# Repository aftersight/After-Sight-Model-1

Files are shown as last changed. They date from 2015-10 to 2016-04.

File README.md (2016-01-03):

# After-Sight-Model-1
Repository for Code/PCB design/3D printed models/Assembly Guide for the After Sight Model 1. go to after-sight.com for additional information

If you would like to contribute, please first go to the raspberry pi forum and post there to introduce yourself. 

https://www.raspberrypi.org/forums/viewtopic.php?f=41&t=49634

What I recommend is to download a current filesystem image. Go to after-sight.com/support

Download the zipped image, extract it, and then burn it to a micro SD card with a program like win32diskimager. 

Put the micro SD into the After Sight Model 1, and fire away. 

If you don't do that, there is a laundry list of dependencies to deal with. 

If you need an after sight model 1 (hardware), email mike.mcwilliams@after-sight.com.

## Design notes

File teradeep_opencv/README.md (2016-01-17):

# demonstration application - Embedded

This is our May 2015 top neural network for large-scale object recognition. It has been trained to recognize most typical home indoor/outdoor objects in our daily life. It was trained with more that 10 M images on a private dataset. It can serve as good pair of eyes for your machines, robots, drones and all your wonderful creations!

<!--[![icon](icon.jpg|width=400px)]-->
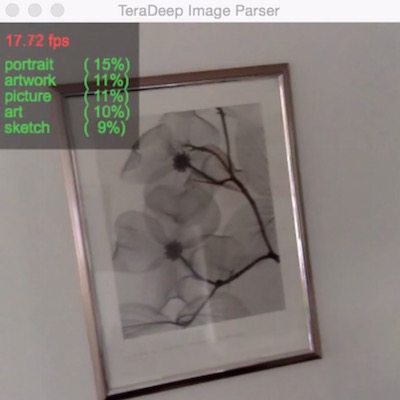
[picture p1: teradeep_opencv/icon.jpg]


See it in action in this [video #1](https://www.youtube.com/watch?v=_wXHR-lad-Q), and also this other [video #2](https://www.youtube.com/watch?v=B0TreumQO-0).

This application is for tinkerers, hobbiest, researchers, evaluation purpose, non-commercial use only.

This library is exclusive for embedded linux and linux machines. For a full PC Torch7 implementation of this same demonstration, see `generic-pc` in this repository. 

It has been tested on ODROID XU4 and Tegra TX1 boards. It can run at > 1 fps on the ODROID XU4, and a lot faster on the Tegra GPU.

## install:
Requirements: libfreetype6-dev, OpenCV.

Install our embedded library thnets: https://github.com/mvitez/thnets

### On ARM:

	git clone https://github.com/mvitez/thnets.git
	cd thnets
	export LD_LIBRARY_PATH=/usr/local/lib
	cd OpenBLAS-stripped
	make
	sudo make install
	cd ..
	make
	sudo make install

### On PC:

Install OpenBLAS first:

	git clone https://github.com/xianyi/OpenBLAS.git
	cd OpenBLAS
	make NO_AFFINITY=1 USE_OPENMP=1
	make install

OpenBLAS will be installed in /opt/OpenBLAS/lib. Install thnets:

	git clone https://github.com/mvitez/thnets.git
	cd thnets
	export LD_LIBRARY_PATH=/usr/local/lib:/opt/OpenBLAS/lib
	make OPENBLASPATH=/opt/OpenBLAS/lib
	sudo make install

Please download files: `model.net`, `categories.txt` and `stat.t7` from https://www.dropbox.com/sh/qw2o1nwin5f1r1n/AADYWtqc18G035ZhuOwr4u5Ea?dl=0

## compile:

	make

or on PC:

	make OPENBLASPATH=/opt/OpenBLAS/lib

## run:

	./thnetsopencvdemo -m <path do directory with model.net>

## usage:

Feel free to modify and use for all you non-commercial projects. Interested parties can license this and other Teradeep technologies by contacting us at `info@teradeep.com`

## most importantly:

Have fun! Life is short, we need to produce while we can!

## credits:
Marko Vitez, Aysegul Dundar, Jonghoon Jin, Alfredo Canziani, Eugenio Culurciello, Berin Martini all contributed to this work and demonstration. Thank you all!

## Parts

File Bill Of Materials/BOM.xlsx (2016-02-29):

Latest Revision: February 16th, 2016
After Sight Model 1 - Bill Of Materials:
Item: | Supplier: | Link to Source: | Price (USD) | Quantity: | Total: | Notes: | Backup Supplier:
Breakaway 0.1" Male Pin Headers | Adafruit | https://www.adafruit.com/products/392 | $4.95 | 1 | $4.95 | The adafruit product has 360 pins in the bunch. We only use 25 pins per custom pcb at rev35. Therefore there will be leftovers, and we can make more. | Mouser
2X20 extra tall stacking header | Adafruit | https://www.adafruit.com/products/1979 | $5.90 | 1 | $5.90 | This component raises the custom PCB high enough to clear the ethernet and USB ports. | None
Powerboost 1000C | Adafruit | https://www.adafruit.com/products/2465 | $19.95 | 1 | $19.95 | Power Manager. Can simultaneously charge the internal battery while supplying power to the system uninterrupted. | None
Raspberry Pi V2 Model B | Adafruit | https://www.adafruit.com/products/2358 | $39.95 | 1 | $39.95 | Brains of the unit | Many Alternative distributors for the rpi foundation
Maxbotix HRLV EZ1 | Adafruit/Maxbotix | http://www.maxbotix.com/documents/HRLV-MaxSonar-EZ_Datasheet.pdf | $32.95 | 1 | $32.95 | Used in serial mode with the back jumper soldered. If you don't solder the back jumper IT WILL NOT WORK with the custom pcb, and you will have to build a signal inversion circuit. Measure distance 0.3-5m | Maxbotix Directly is cheapest at quantity BY FAR, no other manufacturers.
2X18650 lipo cells in parallel with jst connector, 4400 mAh | Adafruit | https://www.adafruit.com/products/354 | $19.95 | 1 | $19.95 | Battery Pack for rev35 Case/PCB | Many Alternatives, and some can be up to double the energy density in the same footprint, much lower prices out there too
Vibration Motor, 5V | Adafruit | https://www.adafruit.com/products/1201 | $1.90 | 1 | $1.90 | Provides Vibration Feedback. Signal from gpio, transistored to power rails, with diode for back emf protection | Many Alternatives
Rotary Encoder Pushbutton | Adafruit | https://www.adafruit.com/products/377 | $4.95 | 1 | $4.95 | includes knob | Many Alternatives
Fancy Knob | Adafruit | https://www.adafruit.com/products/2056 | $3.95 | 1 | $3.95 | OPTIONAL, but nice | Many Alternatives
9 dof accel/gyro/magneto | Adafruit | https://www.adafruit.com/products/1714 | $19.95 | 1 | $19.95 | Used for straight line following application | few alternatives, ex. Sparkfun
1n4001 diode | Mouser | http://www.mouser.com/ds/2/395/1N4001%20SERIES_H14-523306.pdf | $0.26 | 1 | $0.26 | for back emf protection | many manufacturers and suppliers
6X1/8watt resistors | Mouser | http://ca.mouser.com/Passive-Components/Resistors/_/N-5g9n?P=1z0vkomZ1yyxf87 | $0.15 | 6 | $0.90 | resistors for current limiting, and voltage dividers. | many manufacturers and suppliers
BC517 NPN transistor | Mouser | http://www.mouser.com/ds/2/149/BC517-310233.pdf | $0.69 | 1 | $0.69 | signal translation from gpio to vibe motor | many manufacturers and suppliers
BC516 PNP transistor | Mouser | http://www.mouser.com/ds/2/149/BC516-75067.pdf | $0.59 | 1 | $0.59 | used in shutdown circuit | many manufacturers and suppliers
On/On Powerswitch | digi-key | http://www.digikey.com/product-search/en?keywords=40-4169-00 | $5.22 | 1 | $2.17 | case mounted on/on power switch | Few alternatives without case redesign
220 uF electrolytic | mouser | http://www.mouser.com/ds/2/315/ABA0000CE12-465472.pdf | $0.62 | 1 | $0.62 | Timer RC circuit capacitor | many manufacturers and suppliers
100 uF electrolytic | mouser | http://www.mouser.com/ds/2/88/SEK-32248.pdf | $2.68 | 1 | $2.68 | power filter capacitor for maxbotix sensor | many manufacturers and suppliers
3D Printed Case (10 hours est. 100 grams PLA) | unknown | Priced Via Shape Ways = $67. When I print at home in PLA I estimate cost is about 10$ | $67.00 | 1 | $67.00 |  | Do you own a 3D printer? I have printed many cases in PLA for cheap.
M3 screws 0.5X16 mm | Brighton-Best | No Link, available at any good bolt supply store | $0.20 | 4 | $0.80
 |  |  |  |  | $0.00
 |  |  |  |  | $0.00
 |  |  |  |  | $0.00
 |  |  |  |  | $0.00
 |  |  |  |  | $0.00
 |  |  |  |  | $0.00
 |  |  |  |  | $0.00
 |  |  |  |  | $0.00
 |  |  |  |  | $0.00
Total |  |  |  | 27 | $230.12

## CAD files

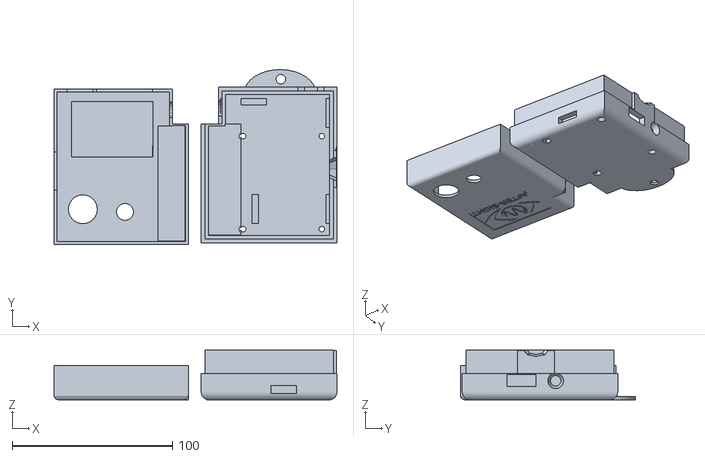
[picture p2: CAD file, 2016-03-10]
3D Models/CaseRevisionMar92016.stl
176.4 x 109.0 x 31.0

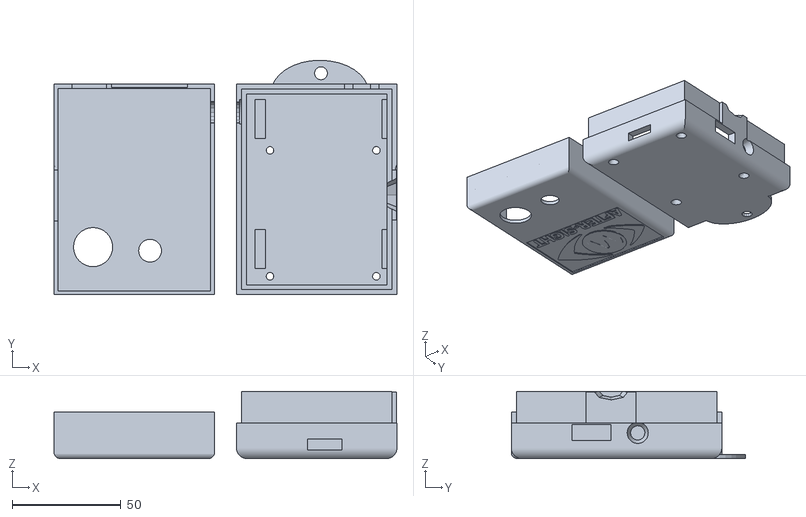
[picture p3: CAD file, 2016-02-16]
3D Models/CaseforPCBrev34.stl
158.0 x 108.0 x 31.0

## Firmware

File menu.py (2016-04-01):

import os #To set working directory properly
import re #import regular expression evaluator
import urllib #Used to test if internet is available
import time #required for sleep pauses
import threading #We will be making threads
import RPi.GPIO as GPIO #We use lots of GPIOs in this program
import datetime #To allow for keeping track of button press length
import subprocess #To launch external processes
import keyPress #Allow for asynchronous keyboard input lifted from http://stackoverflow.com/questions/510357/python-read-a-single-character-from-the-user
from subprocess import call #to launch external processes
import gaugette.rotary_encoder # Lets the rotation be handled with threaded watching
from webcamvideo import WebcamVideoStream #Class for creating a camera thread
from confmanager import ConfManager
from raspivoice import Raspivoice
from teradeep import Teradeep
from facedetect import Facedetect

GPIO.setmode(GPIO.BCM)  #setup for pinouts of the chip for GPIO calls. This will be different for the rotary encoder li$
GPIO.setup(27, GPIO.IN, pull_up_down=GPIO.PUD_UP) #GPIO for detecting low battery
GPIO.setup(25, GPIO.IN, pull_up_down=GPIO.PUD_UP) #Rotary Pushbutton Input
GPIO.setup(9, GPIO.IN, pull_up_down=GPIO.PUD_DOWN) # GPIO for detecting Power Switch Position, used to shtudown system
GPIO.setup(10, GPIO.IN, pull_up_down=GPIO.PUD_DOWN) # GPIO for Detecting External Power State
GPIO.setup(20, GPIO.OUT)   #Define pin 20 as output, for vibration motor
pulses = 3 #make constant short pulses
for i in range(0,pulses):
        GPIO.output(20,True)
        time.sleep(0.05)
        GPIO.output (20,False)
        time.sleep(0.05)


espeak_process = subprocess.Popen(["espeak", "-f","/home/pi/introtext.txt", "--stdout"], stdout=subprocess.PIPE)
aplay_process = subprocess.Popen(["aplay", "-D", "sysdefault"], stdin=espeak_process.stdout, stdout=subprocess.PIPE)
aplay_process.wait() #Forces wait on initial disclaimer reading force wait for short introtext on second and subsequent boots

call (["sudo","cp","/home/pi/altgreet.txt","/home/pi/introtext.txt"]) #After first boot get rid of disclaimer and shorten the greeting


def CheckToClose(k, (keys, printLock)): #This is required for the keyscanning to use the USB number pad
    printLock.acquire()
    print "Close: " + k
    printLock.release()
    if k == "c":                        #While debugging. If you press 'c' once, you can now use ctrl c to terminate the execution
        keys.stopCapture()

t1=0 #t1-t4 used for timing pushbutton events
t2=0 # t2-t4 used as adders amongst a few intervals to allow for assignments of different functions based on time the button is depressed
t3=0 #
t4=0 #The final interval of 7 seconds shuts the device down (software, not electricity). It protects the filesystem and ought to remain

timesinceflip = 0

config = ConfManager() # Load our class with settings from aftersight.cfg

vibration = False #By default vibration is turned off

if config.ConfigVibrationStartup: #If the config file sets rangefinder/vibration for startup, toggle the variable for the vibration motor
        vibration = True

A_Pin=4 #Encoder CC direction
B_Pin=5 #Enconder C direction
encoder = gaugette.rotary_encoder.RotaryEncoder.Worker(A_Pin, B_Pin)#Use worker class to try to catch transitions better.
encoder.start()#start the worker class encoder watcher
encoder.steps_per_cycle = 4 #the encoder always gives 4 for 1 detente

oldexternalpowerstate = 0 # this variable enables an espeak event when the power plug is inserted or removed

Main=["Toggle Raspivoice","Toggle Teradeep","Toggle Distance Sensor","Toggle Face Detection", "Settings","acknowledgements","Disclaimer"]
Settings=["Advance Volume","Raspivoice Settings", "Teradeep Settings","Distance Sensor Settings","Update Software","Return to main menu"]
RaspivoiceSettings = ["Toggle Playback Speed","Toggle Blinders","Advance Zoom","Toggle Foveal Mapping", "Advance Contrast", "Toggle Raspivoice Autostart", "Return to Main Menu"]
TeradeepSettings = ["Next Threshold",  "Toggle Teradeep Autostart","Return to Main Menu"]
DistanceSensorSettings = ["Cycle Feedback Method","Return to Main Menu"]
VolumeMenu = ["Volume Up", "Volume Down", "Return to Main Menu"]

#You can change and add menu items above, but you MUST go to the section where the MenuLevel and menupos are evaluated for a button press/release in under three seconds
#You have to change the actions for the items being evaluated there.
#If you don't, no bueno

bequiet = False #This is old and can be removed, but there is some conditional code below that would have to go at the same time. 
MenuLevel = Main #Select the Main Menu first
menupos = 0 #position in menu list

printLock = threading.Lock() #Setup for keyscanning thread
keys = keyPress.KeyCapture()
keys.startCapture(CheckToClose, (keys, printLock)) #Start the keyboard scanner thread

seconddelta = 0

call (["sudo","espeak","MainMenu,Rotate,Knob,For,Options"])
camera_port = 0 #Open Camera 0
#If your camera doesn't support HD, you'll have to change it here (1280X720)
camera = WebcamVideoStream(src=camera_port, width=640, height=480) #define where I dump camera input

camerastarted = False
raspi = Raspivoice(camera, config)
tera = Teradeep(camera, config)
face = Facedetect(camera, config)
cameraOk = camera.isOk() # Don't call this to often when the camera is stopped, since it will then temporarily init the camera to check it

if config.ConfigRaspivoiceStartup == True and cameraOk:

        camerastarted = camera.start()
        raspi.start()
if config.ConfigTeradeepStartup == True and cameraOk:
        if not camerastarted:
                camerastarted = camera.start()

        tera.start()
if not cameraOk:
	call (["sudo","espeak","No camera detected, check your connections."])

batteryshutdownstarttime = 0 #this will record the time when the shutdhown signal is first recieved
batteryshutdowndetectedflag = 0 #once the low battery signal has been detected once, this flag will stay true. This will avoid situations where the light is cycling
batteryshutdowntime = 300 #give the battery shutdown 300 seconds before forcing a shutdown

while 1:  #Main Loop
    if camera.cameraError and (raspi.running or tera.running):
    	camerastarted = False
    	raspi.stop()
    	tera.stop()
	face.stop()
    	call (["sudo","espeak","There was an error with the camera, stopping applications. Try reconnect the camera, and restart applications"])
    battstate = GPIO.input(27) #check if the battery low state is true or false
    switchstate = GPIO.input(9) #if the pushbutton is depressed, this ought to be true
    externalpowerstate = GPIO.input(10) #has external power been connected or disconnected
    CurrentMenuMaxSize = len(MenuLevel)-1 #Have to subtract one because lists start at zero, but the len function returns only natural numbers

    delta = encoder.get_delta()
    keysPressed  = keys.getAsync()
    #print keysPressed
    if (delta!=0 or keysPressed != []):
        print keysPressed
        #print "rotate %d" % delta

        #The Rotary Encoder has the annoying feature of giving back four delta steps per single detente ~usually~
        #For example, 1,1,1,1 is normal. Quite often it is 1,3 other times 1,2,1 or 1,1,2
        #Using the corrections below, rotations clockwise are normalized to a value of 1
        #Rotations counterclockwise are normalized to -1
        #So the normal output of 1,1,1,1 remains 1,3 becomes 1,1 and 1,2,1 or 1,1,2 become 1,1,1
        #The end result is that most often the values will be 2 or 3, and occasionally 4 after each rotation of one detente occurs
        #the seconddelta variable causes the menu item increase to only happen after the delta accumulates to 3.
        #By changing the top value for seconddelta, responsiveness for single increases changes
        #With a value of three, reliable operation happens

        if delta>0:
                delta=1
        if delta<0:
                delta=-1
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

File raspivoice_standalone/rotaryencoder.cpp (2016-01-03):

/*
Updated version including press switch functionality
based on:
rotaryencoder by astine
http://theatticlight.net/posts/Reading-a-Rotary-Encoder-from-a-Raspberry-Pi/
https://github.com/astine/rotaryencoder
*/
#include <wiringPi.h>

#include <stdio.h>
#include <stdlib.h>
#include <stdint.h>

#include "rotaryencoder.h"
#include <chrono>
void updateEncoders(void);
void updateSwitch(void);

//Pre-allocate encoder objects on the stack so we don't have to 
//worry about freeing them
struct encoder encoders[max_encoders];

int numberofencoders = 0;

void updateEncoders()
{
   struct encoder *encoder = encoders;
   unsigned long nowTime = std::chrono::system_clock::now().time_since_epoch() /
                           std::chrono::milliseconds(1);   
   for (; encoder < encoders + numberofencoders; encoder++)
   {
      int MSB = digitalRead(encoder->pin_a);
      int LSB = digitalRead(encoder->pin_b);

      int encoded = (MSB << 1) | LSB;
      int sum = (encoder->lastEncoded << 2) | encoded;
      if ((nowTime - encoder->lasttime) < 200)
      {

         encoder->lasttime = nowTime;
         encoder->lastEncoded = encoded;
         break;
      }
      encoder->lasttime = nowTime;

      if (sum == 0b1101 || sum == 0b0100 || sum == 0b0010 || sum == 0b1011) encoder->value++;
      if (sum == 0b1110 || sum == 0b0111 || sum == 0b0001 || sum == 0b1000) encoder->value--;

      encoder->lastEncoded = encoded;
   }
}

void updateSwitch()
{
   struct encoder *encoder = encoders;
   unsigned long nowTime = std::chrono::system_clock::now().time_since_epoch() /
                           std::chrono::milliseconds(1);
   
   for (; encoder < encoders + numberofencoders; encoder++)
   {
      int pin_state = digitalRead(encoder->pin_switch);
      if (pin_state == LOW)
      {
         //TODO: Debounce with millis() ? 
         if ((nowTime - encoder->lasttime) > 200)
         {

            encoder->switchpresscount++;
         }
         encoder->lasttime = nowTime;
      }
   }
}

struct encoder *setupencoder(int pin_a, int pin_b, int pin_switch = -1)
{
   if (numberofencoders > max_encoders)
   {
      printf("Maximum number of encodered exceded: %i\n", max_encoders);
      return NULL;
   }

   struct encoder *newencoder = encoders + numberofencoders++;
   newencoder->pin_a = pin_a;
   newencoder->pin_b = pin_b;
   newencoder->pin_switch = pin_switch;
   newencoder->value = 0;
   newencoder->lastEncoded = 0;
   newencoder->switchpresscount = 0;
   newencoder->lasttime = 0;

   pinMode(pin_a, INPUT);
   pinMode(pin_b, INPUT);
   pullUpDnControl(pin_a, PUD_UP);
   pullUpDnControl(pin_b, PUD_UP);
   wiringPiISR(pin_a, INT_EDGE_BOTH, updateEncoders);
   wiringPiISR(pin_b, INT_EDGE_BOTH, updateEncoders);
   if (pin_switch != -1)
   {
      pinMode(pin_switch, INPUT);
      pullUpDnControl(pin_switch, PUD_UP);
      wiringPiISR(pin_switch, INT_EDGE_FALLING, updateSwitch);
   }

   return newencoder;
}

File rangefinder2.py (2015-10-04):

import time
import RPi.GPIO as GPIO
import serial
import datetime
from subprocess import call

time.sleep(5) #This sleep spot is meant to let the preamble espeak for raspivoice finish with less intrusion from this process.
GPIO.setmode(GPIO.BCM)  #setup for PWM
GPIO.setup(20, GPIO.OUT)   #Define pin 20 as output, for PWM modulation of vibration motor
p = GPIO.PWM(20, 25)  #channel = 20 , frequency = 25 hz
p.start(5) #5% duty cycle to start. should immediately change as the rangefinder reads
GPIO.setup(27, GPIO.IN, pull_up_down=GPIO.PUD_UP) #GPIO for detecting low battery
GPIO.setup(25, GPIO.IN, pull_up_down=GPIO.PUD_UP) #Rotary Pushbutton Input
GPIO.setup(9, GPIO.IN, pull_up_down=GPIO.PUD_DOWN) # GPIO for detecting Power Switch Position, used to shtudown system
GPIO.setup(10, GPIO.IN, pull_up_down=GPIO.PUD_DOWN) # GPIO for Detecting External Power State
maxbotix = serial.Serial("/dev/ttyAMA0",baudrate=9600,timeout=5) #Open a serial input to recieve from the maxbotix ultrasonic sensor
time.sleep(0.2)#This sleep interval is required to let the serial input open completely before it is read for the first time. Without this pause, random crashes on startup occur
t1=0 #t1-t4 used for timing pushbutton events
t2=0
t3=0
t4=0
vibration=-1 #vibration starts off. Changing this = 1 starts vibration based on distance measurement
timesinceflip = 0
oldexternalpowerstate = 0 # this variable enables an espeak event when the power plug is inserted or removed
while 1:
    maxbotix.flushInput() #clear buffer to get fresh values if you don't do this, you won't get responsive readings
    currdistance = maxbotix.readline(10) #Take ten characters worth of the serial buffer that accumulates since the flush
    stripstart = currdistance.find("R") #Look for the character "R", find out where it occurs in the string first
    stripend = stripstart + 5 #Define the end of the character length we need to grab the numeric info
    currdistance = currdistance[stripstart+1:stripend] #strip out the numeric info
    currmm = float(currdistance) #Now make the info a number instead of a string
    print currmm #comment this out after debugging
    battstate = GPIO.input(27)
    switchstate = GPIO.input(9)
    externalpowerstate = GPIO.input(10)
    if (externalpowerstate != oldexternalpowerstate):
        print ('External Power State Changed')
        if(externalpowerstate == 1):
                print ('External Power Connected')
                call (["sudo","espeak","ExternalPowerConnected"])
        elif (externalpowerstate ==0):
                print ('External Power Disconnected')
                call (["sudo","espeak","ExternalPowerDisconnected"])
    if (externalpowerstate == 0):
        print ('External Power Disconnected, Running from Internal Battery')
    if (switchstate == 1):
        print ('Power Switch Turned Off, System Shutdown Initiated')
        call (["sudo", "espeak", "shutdown"])
        call (["sudo", "shutdown", "-h", "now"])
    if (switchstate == 0):
        print ('Power Switch Is On, Keep Working')
    if (battstate == 1):
        print ('Battery OK, keep system up')
    if (battstate == 0):
        print ('Battery Low, System Shutdown')
    if (vibration == 1):
        #print "vibration on"
        if (currmm > 300 and currmm < 600):
                p.ChangeFrequency(5)
                p.ChangeDutyCycle(50)
        if (currmm > 600 and currmm < 1000):
                p.ChangeFrequency(7)
                p.ChangeDutyCycle(50)
        if (currmm > 1000 and currmm < 2000):
                p.ChangeFrequency(10)
                p.ChangeDutyCycle(50)
        if (currmm > 2000 and currmm < 3000):
                p.ChangeFrequency(20)
                p.ChangeDutyCycle(50)
        if (currmm > 3000 and currmm < 4000):
                p.ChangeFrequency(30)
                p.ChangeDutyCycle(50)
        if currmm > 4000:
                p.ChangeFrequency(40)
                p.ChangeDutyCycle(50)
    elif (vibration == -1):
        p.ChangeDutyCycle(0)
        #print "Vibration Off
    if GPIO.input(25):
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

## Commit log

2015-10-04 Create rangefinder2.py
    This collection of routines causes the After Sight Model 1 to monitor the GPIO of the raspberry pi. The GPIO look for the rotary encoder button press, and start a timer to toggle the vibration/range 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
2015-10-04 Added untested 3D case file
    Initial commit of the model for the After Sight Model 1
    [Oct4thUntested.stl]
2015-10-05 First Submission of PCB design for Fritzing
    The PCB lets you make the raspberry pi an embedded system
    [vOICeOnPi-Rev33.fzz]
2016-01-03 Jan 2nd Commit - Fork raspivOICe, created menu and control process, added jetpac, added persistent config
    [vOICeOnPi-Rev33.fzz, vOICeOnPi-Rev34.fzz]
2016-01-18 Moved the previous raspivoice to standalone since the new doesn't use the camera directly + added the new code that uses image files
2016-01-27 added blinders,zoom,and foveal mapping to raspivoice settings. Added triple vibration on startup, removed --speak from raspivoice execution
    added config items for blinders zoom and foveal mapping, added those
    choices to the menus.
    the triple vibration on startup is to let users know the device is
    working even if their audio is not
    removed --speak from raspivoice execution: this change allows the
    keyboard to be used without crashing raspivoice. However you have to
    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
2016-02-04 Better handling for camera disconnection, and spoken messages when trying to use the camera when no camera detected
2016-02-15 Added Facial Detection
    I have tried to make a way to classify position of the face in a 3x3
    grid It doesn't work perfectly, but I found it reliable for detecting
    when a face is present, and if I am centered on the face with the
    camera. Thinking about adding a depth feature as the rectangle size
    changes with distance on the average adult head.
2016-02-16 Updated PCB design
    deleted pcb mounted pushbutton on/on switch. moved components.
    added 9 degree of freedom accel/gyro/magneto sensor tie in. powered from
    3.3v pin from rpi gpio.
    communicates via i2c.
    [AfterSightModel1-Rev35.fzz]
2016-02-16 Case Model File compatible with revision 34 PCB
    This case model file will be changed to house a larger battery. This is
    more for historic record.
    [CaseforPCBrev34.stl, Oct4thUntested.stl]
2016-02-20 bill of materials for makers
    detailed BOM for makers. Has links to sources, and makes suggestions
    [BOM.xlsx]
2016-02-29 detailed BOM
    With links to or info about suppliers or potential suppliers
    [BOM.xlsx]
2016-03-10 Revised Case for Updated PCB Rev 35
    Enlarged area for new battery
    [CaseRevisionMar92016.stl]
2016-03-26 Implemented Automatic Core Update
    Added Update command to settings menu. it does a git pull, and then runs
    all core update scripts to rebuild/recopy raspivoice, teradeep, and the
    facialdetection. The distancesensor is updated as part of the home
    directory scripts as it doesn't need it's own folder.
    installdeps is meant to keep the devices up to date. Once an apt-get
    package is installed, a hold is placed on it to prevent the loss or
    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
2016-03-27 needed to alter some commands used to set current directory
    if you use sudo you cant change directories apparently.
2016-04-01 Used Peter Meijer's Contrast Algorithm in RaspiVoice.cpp
    Also updated menu,py to allow for settings 0,1,2,3 under raspivoice
    settings menu
    converted an espeak command during updating to a console print command
    when one time update scripts that have already been run are encountered
    in menu.py
    I tested the compilation prior to committing and it seemed fine. Will
    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
